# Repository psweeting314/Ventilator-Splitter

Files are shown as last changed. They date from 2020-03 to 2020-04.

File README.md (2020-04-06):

# Ventilator-Splitter

************************************************************************************************************************************
ALL INFORMATION AND PLANS PROVIDED ARE TO BE USED AT HEALTHCARE PROVIDERS’ AND HOSPITALS’ OWN RISK. THESE METHODS AND DEVICES REMAIN CLINICALLY UNTESTED AND ARE EXPERIMENTAL. THEY ARE NOT APPROVED BY THE FDA OR OTHER MEDICAL LICENSING BODIES. 
************************************************************************************************************************************

A splitter and accessories for multiple patients to share a single ventilator

Kits - Each complete kit should contain the following:

  4 - Two way Y splitter

  2 Male - Female PVC adapter

  2 Male - Male PVC adapter
  
Material - Petg preferred PLA acceptable 

Additional Specifications

  .3mm max layer height
  
  2 walls
  
  20% infill
  
  No supports
  
  seams exposed as opposed to hidden

These files are shared for the purpose of helping medical professionals treat COVID-19 patients by splitting the output and input from a single ventilator among multiple patients. This was designed to replace the network of tubes and tees that some hospitals are using to accomplish this. It does not include any filtration or valving, but is designed to have clearance for 90mm diameter filters. The inlet is a 22mm female socket, and the 4 outlets are 22mm spigot connections. This is an EXPERIMENTAL design which has NOT BEEN TESTED ON HUMANS.

It is designed to be printed in PETG on an FDM 3D printer. On a Prusa i3 M3S it prints in about 3:30, using 0.3mm layer height and no supports. It should also be printable on SLA and MSLA machines with sufficient build volume.

As of 3/21/2020, this has been tested for dimensional accuracy on a Prusa i3 Mk3S and printability. This will be updated.
On 3/22/2020, I added a 2 way splitter for ventilators which cannot support 4. I also added some Male-Male and Male-Female adapters so standard ½” pipe (PVC, copper), can be used. These are friction fit as of now, but PVC could be glued.
On 3/24/2020 received confirmation that it fits on ventilators.

	3/30/2020 Launched GitHub

	   Designed by Philip Sweeting (PSS Innovations), with help from Garret Garner. 

pssinnovationsllc@gmail.com

During this trying medical emergency Keep Breathing NYC and PSS Innovations, LLC have provided this information to support the important work of doctors and hospital support staff. However, the information and plans provided are not a substitute for the experience and advice of licensed medical professionals.

ALL INFORMATION AND PLANS PROVIDED ARE TO BE USED AT HEALTHCARE PROVIDERS’ AND HOSPITALS’ OWN RISK. THESE METHODS AND DEVICES REMAIN CLINICALLY UNTESTED AND ARE EXPERIMENTAL. THEY ARE NOT APPROVED BY THE FDA OR OTHER MEDICAL LICENSING BODIES. 

This website is compiled from a variety of sources and is not considered complete. 

This information is provided without any warranties, whether expressed or implied. Keep Breathing NYC and PSS Innovations, LLC, DISCLAIM ALL REPRESENTATIONS AND WARRANTIES, regarding any information or other material displayed, whether authored by the Keep Breathing NYC team or others.

If you have a medical emergency, call your doctor immediately.

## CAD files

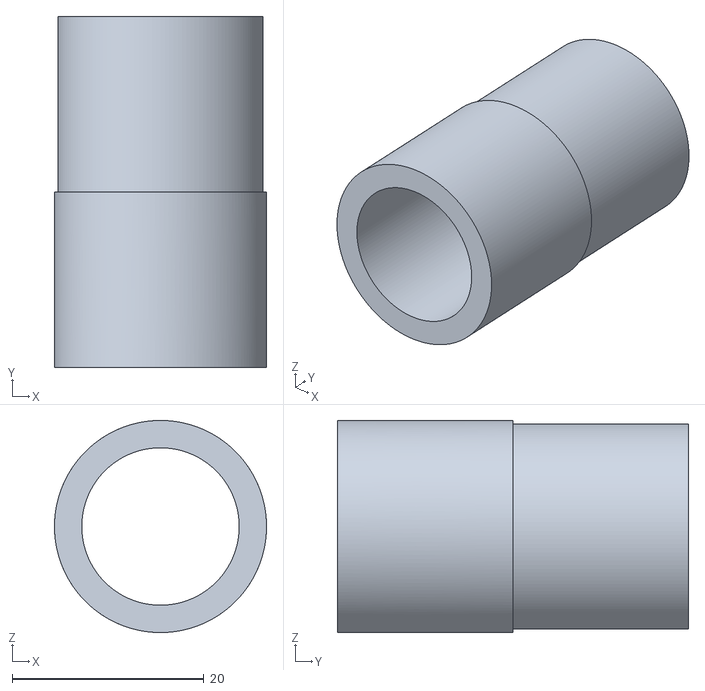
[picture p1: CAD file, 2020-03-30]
0.5in PVC to 22mm Adapter male male.stl
22.1 x 36.6 x 22.1

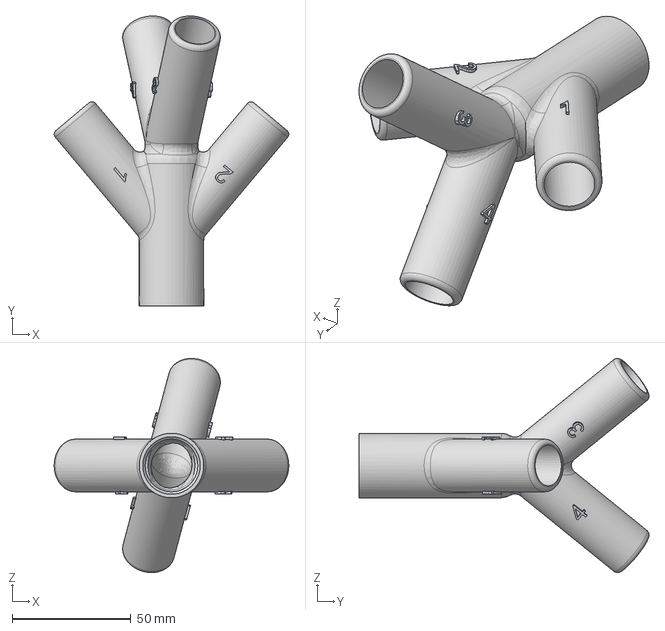
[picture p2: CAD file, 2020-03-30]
CAD Files/Tree Adapter Angled v5.step
98.9 x 122.3 x 90.3 mm

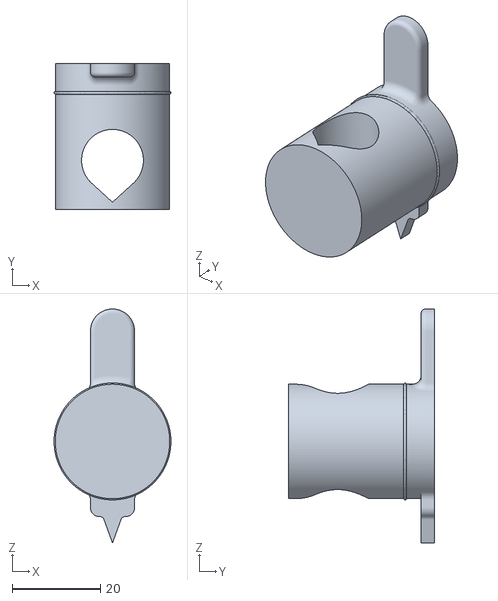
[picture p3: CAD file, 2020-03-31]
Cylinder Valve (Calibrated Printers Only/Cylinder Valve Plug.stl
26.5 x 33.0 x 53.0

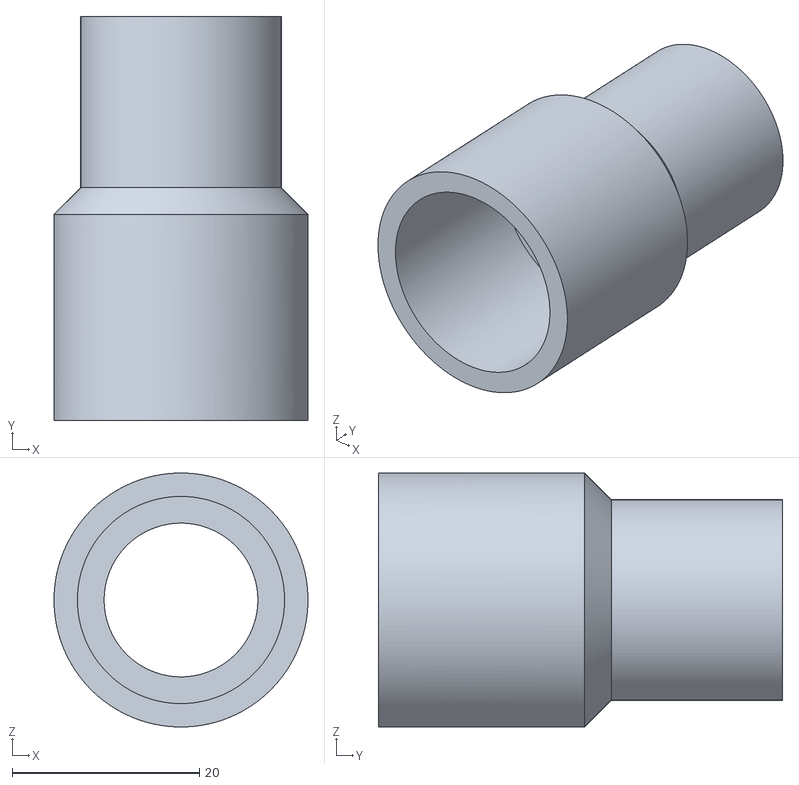
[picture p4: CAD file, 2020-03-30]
0.5in PVC to 22mm Adapter male female.stl
27.1 x 43.1 x 27.1

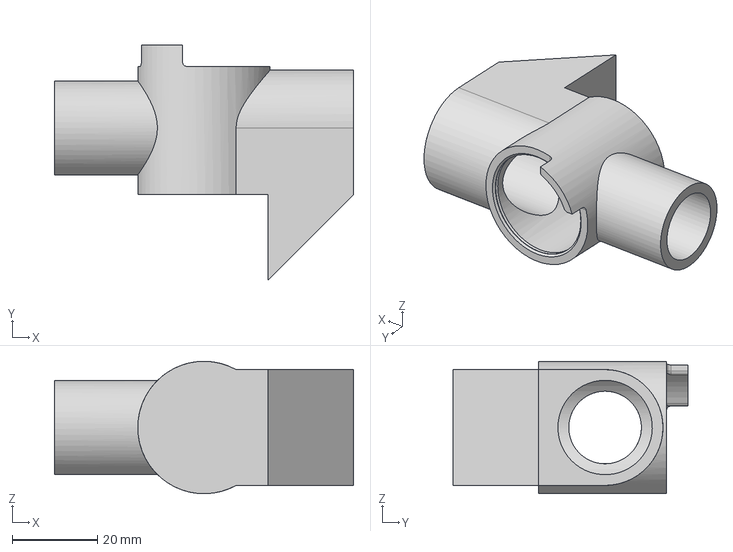
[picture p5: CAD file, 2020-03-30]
CAD Files/Cylinder Valve Body v13.step
70.0 x 55.0 x 31.0 mm

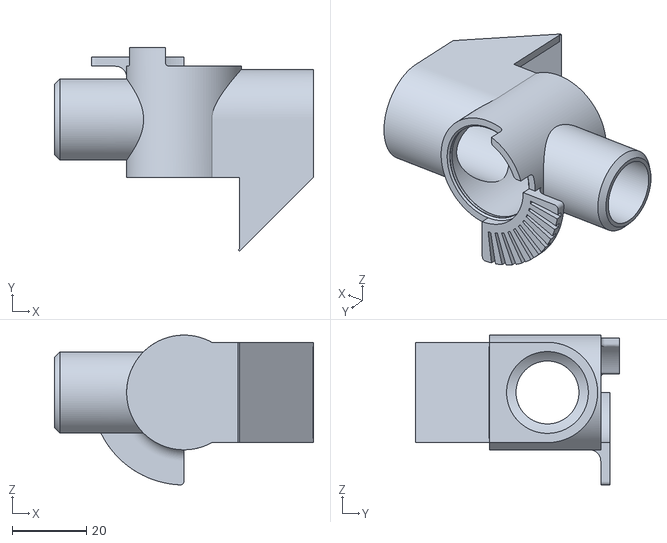
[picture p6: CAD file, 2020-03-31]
Cylinder Valve (Calibrated Printers Only/Cylinder Valve Marked.stl
70.0 x 55.0 x 40.5

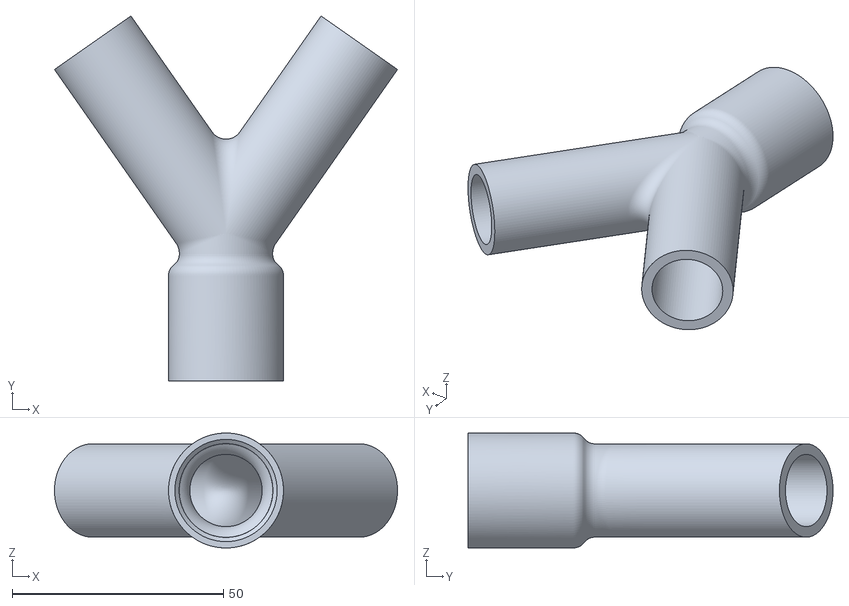
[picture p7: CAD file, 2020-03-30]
2 way splitter.stl
81.2 x 86.4 x 27.2

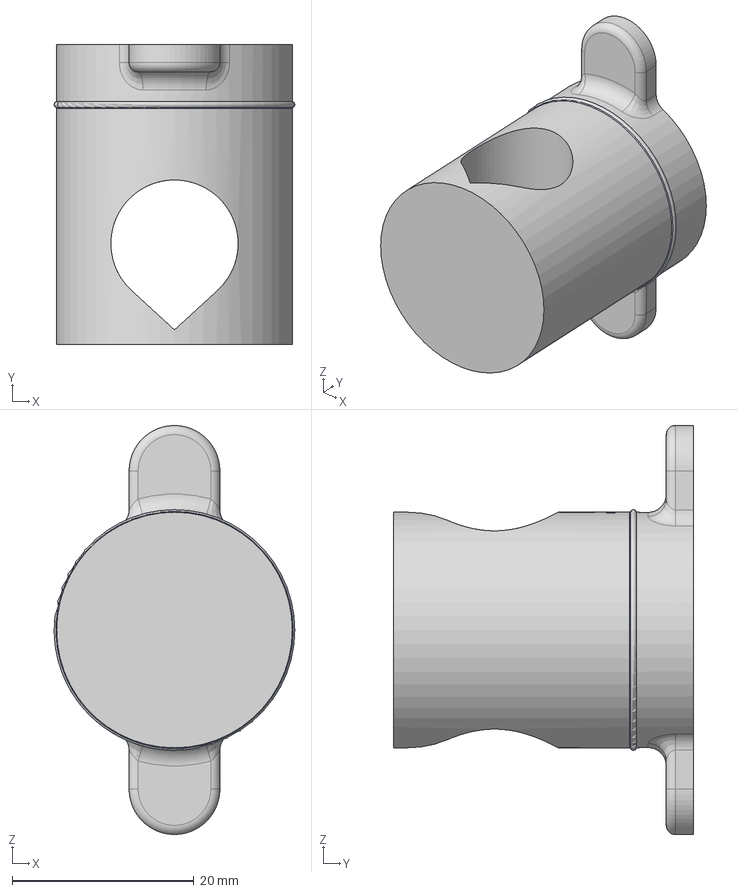
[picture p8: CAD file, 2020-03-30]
CAD Files/Cylinder Valve stopper v13.step
26.5 x 33.0 x 45.0 mm

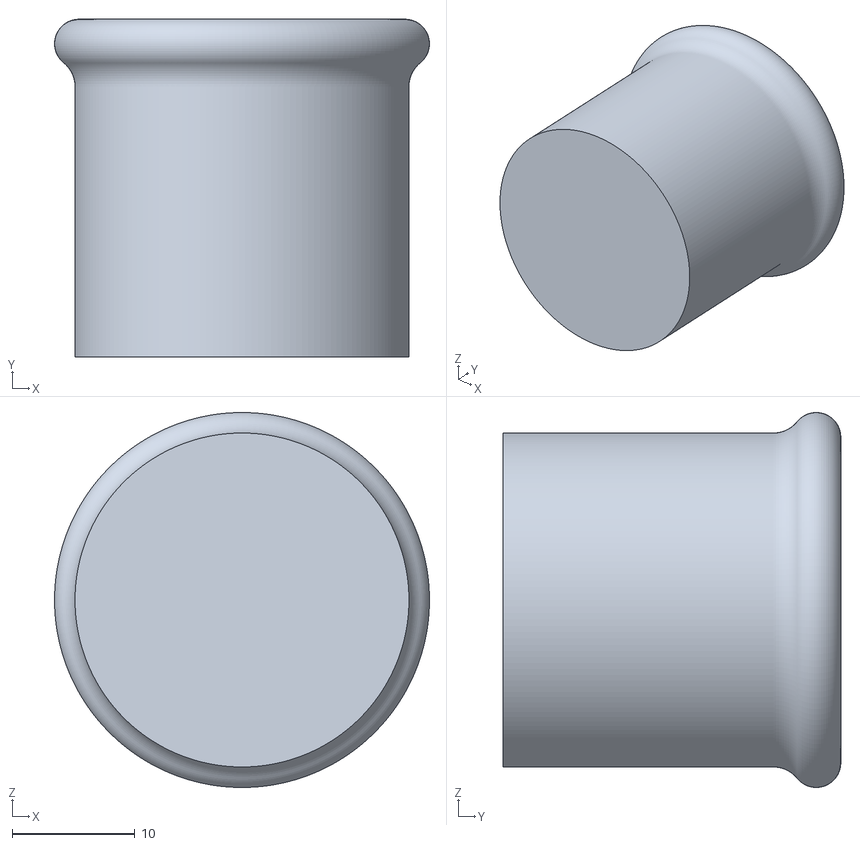
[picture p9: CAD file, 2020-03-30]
ventilator endcap.stl
30.5 x 27.5 x 30.5

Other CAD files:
CAD Files/2 way splitter v4.step
Ventilator Tree Labelled.stl
CAD Files/2 way splitter v4.f3d
CAD Files/Cylinder Valve Body v11.f3d
CAD Files/Cylinder Valve stopper v11.f3d
CAD Files/Tree Adapter Angled v5.f3d

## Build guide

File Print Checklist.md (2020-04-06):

# 3D Print Checklist 1.0
KEEP BREATHING - NYC [Ventilator-Splitter](https://github.com/psweeting314/Ventilator-Splitter)

## Kits

Each complete kit 3.0 should contain the following:

| Qty | Item |
|:---|:---|
| 4 | Two-way Y splitter |
| 2 | Male-to-female PVC adapter |
| 2 | Male-to-male PVC adapter |

## Print Specifications

* Material: PETG preferred or PLA 
* 0.3 mm max layer height
* 2 walls
* 20% infill
* No supports
* Seams exposed as opposed to hidden

## Additional Instructions and Tips

* Compare prints ID and OD with calipers to diagram to ensure that your tolerances
	* Female/input/ID = 22.0mm (+0.2mm/-0.0mm)
	* Male/output ends/OD = 22.0mm (+0.0mm/-0.2mm)
* If possible, sterilize each piece with isopropanol 
* Place full kit into Ziplock baggie
* Update inventory spreadsheet

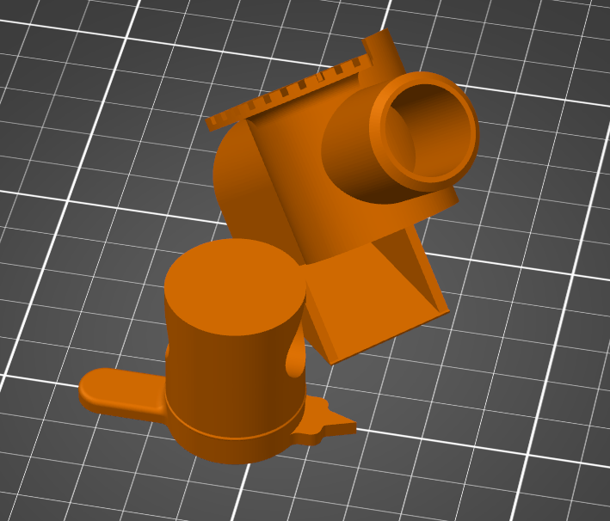
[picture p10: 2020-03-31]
Cylinder Valve (Calibrated Printers Only/Cylinder Valve Print Orientation.PNG

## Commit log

2020-03-30 Standard Kit STLs added
    [0.5in PVC to 22mm Adapter male female.stl, 0.5in PVC to 22mm Adapter male male.stl, 2 way splitter.stl, Ventilator Tree Labelled.stl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]
2020-03-30 Update and rename README.md to Print Checklist.md
2020-03-31 Update Print Checklist.md
2020-03-31 Create Cylinder Valve Instructions
2020-03-31 Update Cylinder Valve Instructions
2020-04-01 Formatted printing checklist
